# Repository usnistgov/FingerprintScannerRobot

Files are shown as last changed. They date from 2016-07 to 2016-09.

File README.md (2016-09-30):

# Fingerprint Scanner Robot v1.0

Welcome to the Fingerprint Scanner Robot project! This project is comprised of two robots to test fingerprint scanners. The first robot is the Networked Automated Fingerprint Scanner Test Robot (NAFSTR), and the second is the Networked Automated Rolled Fingerprint Scanner Test Robot (NARFSTR). Both robots were designed and built at the National Institue of Standards and Technology (NIST) as part of the [Biometric Web Services](http://www.nist.gov/itl/iad/ig/bws.cfm) project. The NAFSTR was designed and built by Jacob Glueck as part of the Summer High School Intern Program (SHIP) over the summer of 2014 and the NARFSTR was designed and built by Jacob Glueck during his time as a  Pathways Intern from October 2014 to July 2015 for the Biometric Web Services project. Kevin Mangold served as Jacob's mentor during both projects.

For more information, check out the documentation  at `Documentation/build/html/index.html` or `Documentation/build/latex/FingerprintScannerRobot.pdf`.

For a video of the NAFSTR, see: https://youtu.be/lXbDDAqTphQ.

For a video of the NARFSTR, see: https://youtu.be/WPvg-6ALE24.

## Project Contents:

For more detailed information and usage/installation details, see the Documentation/build artifacts.

* Circuit: contains all the files related to the robots' circuitry.
* Code: contains all the code
    * CSSharpLibrary: contains a Visual Studio C# solution with the CSharpLibrary for controlling the NAFSTR.
    * FingerprintRobotControl: contains an Eclipse Java project for controlling the robot.
    * FingerprintRobotLocalControl: contains all the C++ code that runs on the robots.
        * lib: libraries the code needs.
        * MACUploader: contains a program for uploading MAC addresses to the robots.
        * NAFSTRLocalControl: contains the program that controls the NAFSTR.
        * NARFSTRLocalControl: contains the program that controls the NARFSTR.
        * TestCode: contains test code.
* Documentation: contains all the documentation.
    * build: contains all the files for the built documentation.
    * source: contains all the source files for the documentation.
* DocumentationOld: contains the communication protocol for the NAFSTR, which is old.
* Final STL Files: contains all the STL files need to print parts for the robot.
* Fingerprints: contains all the files relating to fingerprints for the two robots.
    * NAFSTRSimpleFingerprints: contains all the files for the NAFSTR's fingerprints.
    * NARFSTRRolledFingerprints: contains all the files for the NARFSTR's rolled fingerprints.
    * PointCloudFingerprints: contains all the files for point cloud fingerprints.
* Improvements: contains files relating to improvements that need to be done.
* Pictures: contains pictures of the robots.
* Renderings: contains renderings of the robot.
* RobotLabels: contains files related to the information labels on the robots.
* Sketchup Files: contains the design files for the robots.
* Test STL Files: contains all the STL files used in test prints.
* Test Moves: contains text files with test commands for the two robots.
* Videos: contains videos of the robots.

## Contact:
Kevin Mangold (kevin.mangold@nist.gov)

## Credits:
Primary Developer: Jacob Glueck  
Support: Kevin Mangold

## Disclaimer:
See the NIST dislacimer at https://www.nist.gov/disclaimer.

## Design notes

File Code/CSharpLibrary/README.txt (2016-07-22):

1.	Move: the superclass of PositionMove and SensorMove. Represents a move as specified in the Arduino - Computer Communication Protocol.
2.	PositionMove: represents a position move as specified in the Arduino - Computer Communication Protocol.
3.	SensorMove: represents a sensor move as specified in the Arduino - Computer Communication Protocol.
4.	NAFSTR: represents a robot. Contains methods for each of the robot's commands.

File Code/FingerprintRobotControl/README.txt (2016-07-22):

This Java program allows for easy control of the robot.

1.	Instructions:
	To launch the GUI version, pass in no arguments. To launch the command line version, pass in two arguments. First, the name of the text file which contains the commands. Second, the location of the Arduino to connect to or the autoconnect preference. Acceptable values are a serial port name, an IP address, ethernet, or usb. "ethernet" sets the autoconnect preference to Ethernet and "usb" set the autoconnect preference to USB.
2. Classes:
	2.1	Arduino: represents a robot and is used to control the NAFSTR.
	2.2	ArduinoCom: represents a way of communicating with an Arduino.
	2.3	Command: represents an action that an Arduino can execute.
3. Javadoc: for more documentation, see the Javadoc at /doc/index.html

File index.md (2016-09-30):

---
layout: default
title: "Fingerprint Scanner Robot"
---
<script async type="text/javascript" id="_fed_an_ua_tag" src="https://dap.digitalgov.gov/Universal-Federated-Analytics-Min.js?agency=NIST&subagency=github&pua=UA-42404149-54&yt=true&exts=ppsx,pps,f90,sch,rtf,wrl,txz,m1v,xlsm,msi,xsd,f,tif,eps,mpg,xml,pl,xlt,c"></script>
# Fingerprint Scanner Robot v1.0

Welcome to the Fingerprint Scanner Robot project! This project is comprised of two robots to test fingerprint scanners. The first robot is the Networked Automated Fingerprint Scanner Test Robot (NAFSTR), and the second is the Networked Automated Rolled Fingerprint Scanner Test Robot (NARFSTR). Both robots were designed and built at the National Institue of Standards and Technology (NIST) as part of the [Biometric Web Services](http://www.nist.gov/itl/iad/ig/bws.cfm) project. The NAFSTR was designed and built by Jacob Glueck as part of the Summer High School Intern Program (SHIP) over the summer of 2014 and the NARFSTR was designed and built by Jacob Glueck during his time as a  Pathways Intern from October 2014 to July 2015 for the Biometric Web Services project. Kevin Mangold served as Jacob's mentor during both projects.

For more information, check out the documentation  at `Documentation/build/html/index.html` or `Documentation/build/latex/FingerprintScannerRobot.pdf`.

For a video of the NAFSTR, see: https://youtu.be/lXbDDAqTphQ.

For a video of the NARFSTR, see: https://youtu.be/WPvg-6ALE24.

## Project Contents:

For more detailed information and usage/installation details, see the Documentation/build artifacts.

* Circuit: contains all the files related to the robots' circuitry.
* Code: contains all the code
    * CSSharpLibrary: contains a Visual Studio C# solution with the CSharpLibrary for controlling the NAFSTR.
    * FingerprintRobotControl: contains an Eclipse Java project for controlling the robot.
    * FingerprintRobotLocalControl: contains all the C++ code that runs on the robots.
        * lib: libraries the code needs.
        * MACUploader: contains a program for uploading MAC addresses to the robots.
        * NAFSTRLocalControl: contains the program that controls the NAFSTR.
        * NARFSTRLocalControl: contains the program that controls the NARFSTR.
        * TestCode: contains test code.
* Documentation: contains all the documentation.
    * build: contains all the files for the built documentation.
    * source: contains all the source files for the documentation.
* DocumentationOld: contains the communication protocol for the NAFSTR, which is old.
* Final STL Files: contains all the STL files need to print parts for the robot.
* Fingerprints: contains all the files relating to fingerprints for the two robots.
    * NAFSTRSimpleFingerprints: contains all the files for the NAFSTR's fingerprints.
    * NARFSTRRolledFingerprints: contains all the files for the NARFSTR's rolled fingerprints.
    * PointCloudFingerprints: contains all the files for point cloud fingerprints.
* Improvements: contains files relating to improvements that need to be done.
* Pictures: contains pictures of the robots.
* Renderings: contains renderings of the robot.
* RobotLabels: contains files related to the information labels on the robots.
* Sketchup Files: contains the design files for the robots.
* Test STL Files: contains all the STL files used in test prints.
* Test Moves: contains text files with test commands for the two robots.
* Videos: contains videos of the robots.

## Contact:
Kevin Mangold (kevin.mangold@nist.gov)

## Credits:
Primary Developer: Jacob Glueck  
Support: Kevin Mangold

## Disclaimer:
See the NIST disclaimer at https://www.nist.gov/disclaimer.

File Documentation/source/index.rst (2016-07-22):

.. Fingerprint Scanner Robot documentation master file, created by
   sphinx-quickstart on Wed Jul 15 08:23:43 2015.
   You can adapt this file completely to your liking, but it should at least
   contain the root `toctree` directive.

Welcome to Fingerprint Scanner Robot's documentation!
=====================================================

.. toctree::
  :maxdepth: 2

  intro
  NARFSTR
  NAFSTR
  ProgramDevelopment
  Use

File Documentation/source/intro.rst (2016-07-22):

############
Introduction
############

The fingerprint scanner robots are designed to automatically test fingerprint scanners. There are two robots:

#. NAFSTR: Networked Automated Fingerprint Scanner Test Robot. A robot with four individually-actuated fingers that simulates simple fingerprinting.
#. NARFSTR: Networked Automated Rolled Fingerprint Scanner Test Robot. A robot that simulates rolling a finger across a fingerprint scanner.

Both robots are controlled by an Arduino Uno, and have an Arduino Ethernet Shield. They accept commands sent over USB and over a network.

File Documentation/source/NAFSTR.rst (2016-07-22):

.. include:: <isonum.txt>
.. include:: <isogrk1.txt>

######
NAFSTR
######

**Note:** The documentation below is sparse and needs to be improved. Have fun!

Design
======

Here is an image showing the main parts of the robot:



Here is an exploded view of the robot, which is helpful for assembly:



Here is an image showing how the finger attaches to the servo and how the fingerprint attaches to the finger:



Here is an image showing how the robot rests on the fingerprint scanner:



Here is a final image showing how the electronics housing is assembled:



Construction
============

To construct the robot, first print appropriate quantities of the parts in ``Final STL Files/NAFSTR``\ . Then, attach all the parts together and insert all the electronics. Here is a parts list of all the required parts that are not 3D printed:

.. csv-table:: Parts of NAFSTR
  :file: NAFSTRParts.csv
  :widths: 40,40,6,6,6
  :header-rows: 1

Electronics
===========

To assemble to electronics, look at the Fritzing file located at: ``Circuit/NAFSTRCircuit.fzz``\ .

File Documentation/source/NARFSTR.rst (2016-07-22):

.. include:: <isonum.txt>
.. include:: <isogrk1.txt>

#######
NARFSTR
#######

******
Design
******

Structure
=========

The robot has four adjustable legs, which support a linear actuator, the electronics, and the fingerprint assembly. The following image labels all the main parts:



Fingerprint Assembly
--------------------

The fingerprint consists of a fingerprint, held by two supports. A roller rolls over the fingerprint, pressing it against the scanner. The following image shows how it works:



The linear actuator pulls the roller towards the button. As the roller moves, it compresses the fingerprint against the scanner, causing the scanner the capture a rolled print. Once the moving assembly (consisting of the roller and its support structure) hits the button, the linear actuator stops, and then reverses.

Electronics Box
-------------------
The electronics box contains openings for all the connections and buttons on the robot. The following picture shows all the main features:



There are also four more openings on the back. These are to allow the linear actuator and the button in the fingerprint assembly to connect to the electronics in the box. The following image shows these connections:



************
Construction
************

Parts
=====

3D Printed Parts
----------------

Almost all of the parts for the robot are 3D printed. The STL files for the parts are located in ``Final STL Files/NARFSTR``\ . All of the 3D printed parts were printed in PLA except for the fingerprints. (For more information abou the fingerprints, see :ref:`fingerprintsection`\ .) The PLA parts were printed with a layer height of 0.2 mm using MakerBot's "Standard" profile. We used a MakerBot Replicator 2 and a  5\ :superscript:`th` Generation Replicator. The following table lists each part's name and quantity.

.. csv-table:: 3D Printed Parts
  :file: NARFSTR3DPrintedPartsList.csv
  :widths: 100, 25
  :header-rows: 1

Electronic Parts
-----------------

The following table lists all the electronic parts. Parts that are marked with \* are close to the parts I used, but may not be exact. This is because the parts I used came from kits or other sources, and I was unable to determine their exact information. For the male and female banana plugs, 3 different colors are recommended: 1 red, 1 black, 2 blue.

.. csv-table:: Electronic Parts
  :file: NARFSTROtherPartsList.csv
  :widths: 50, 16, 16, 16
  :header-rows: 1

Screws and Miscellaneous Parts
------------------------------

I did not order these parts, and so have limited information about them.

.. csv-table:: Screws and Miscellaneous Parts
  :file: NARFSTRScrewsAndFeet.csv
  :widths: 100 30 30
  :header-rows: 1

Here is a picture of the screws:



From now on, I will refer to the screws by their color.

Legs and Actuator Mount Assembly
================================

Legs
----

There are two leg assemblies: one on the side of the actuator with the motor, and one on the other side. Both are assembled the same way, but they use different leg adapters. To assemble a leg assembly, first screw a lock nut onto the threaded bolt in the center of the lower adjustable foot. Repeat for the other leg. Then, put an upper adjustable foot piece on top of each lower adjustable foot piece. Push down until the lock nut clicks, locking the lower part to the upper part. Then, insert a bolt head into the square hole on top of each upper adjustable foot. Screw the square head into the bolt using one of the black screws. Finally, connect each foot assembly to the lower part of a leg adapter. Secure the connection by screwing golden screws into the holes on the upper adjustable foot. Repeat this process with the other leg adapter to make the other leg assembly.



Actuator Mounts
---------------

There are two actuator mounts: one for the side of the actuator with the motor, and one for the other side.

Motor End Actuator Mount
""""""""""""""""""""""""

Slide the actuator into the mount. Insert the motor end actuator key into the hole in the actuator mount. Make sure the arrows point towards each other. Secure the key with a golden screw.



Finger End Actuator Mount
"""""""""""""""""""""""""

Slide the actuator into the mount. Insert the finger end actuator key into the hole in the actuator mount. Make sure the arrows point towards each other. Attach the top actuator strap to the actuator using two golden screws.



Insert the bottom actuator strap as shown in the diagram below. Secure it with two black screws. Finally, screw a golden screw into the hole labeled "Screw Hole for Actuator Key" on the diagram below. This secures the key.



Put a 12 mm push button into the button hole on the actuator mount. Secure the button using the button strap and two black screws.



Insert the finger end fingerprint mount and the motor end fingerprint mount into the bottom of the actuator mount. Secure each one with two black screws. Then, insert a fingerprint clip into each of the fingerprint mounts.



Connecting the Legs and Actuator Mounts
---------------------------------------

Insert the leg assemblies into the bottom of the actuator assembly. Secure each leg assembly with two golden screws.



Rubber Feet
-----------

Insert two rubber feet into the bottom of each foot.

Fingerprint Assembly
====================

Glue fingerprint roller A into fingerprint roller B using super glue. Let dry. Connect fingerprint roller to moving base with the exterior finger supports. Secure each support with two black screws. Insert the button pusher into the moving base.



Attach the fingerprint assembly to the actuator by first aligning the four holes on the moving base with the holes on the actuator, ensuring that the button pusher faces the button. Then, screw a silver screw into each of the four holes on the moving base.



Electronics Box Assembly
========================

**Note:** assemble the electronics before assembling the box.

Slide Arduino Uno (with Arduino Ethernet Shield) into the box. Screw female banana plugs into holes of electronics housing. If using colors, put a red jack and a black jack into the top row, and put two blue jacks in the bottom row. Then, super glue the LED cap into the LED hole.



Super glue the front tab onto the bottom of the electronics box.



Assemble the top lid by inserting the power switch and the trigger switch into their holes. The power switch is the green rocker switch, and the trigger switch is the red push button. Using epoxy, glue a 12 mm button into the DHCP reset button hole. The square base of the button should be glued onto the plastic square on the bottom of the top lid.



Assemble the power jack by inserting a female power pigtail into the power jack holder. This may require some force. Screw power jack holder into electronics box using a black screw.



Put all other electronics into the box in the empty area behind the Arduino and put LED into LED cap. Ensure that everything is properly connected. Then, put top on box and secure with two black screws. Put back side on box and secure with one black screw. Finally, connect all cables.

***********
Electronics
***********

Design
======

The robot is controlled by an Arduino Uno microcontroller. On top of the Arduino, there is an Arduino Ethernet Shield, which, through its single Ethernet port, allows the robot to connect to a network. The following components are connected to the Arduino through the header pins on the shield:

#. RGB LED: serves as an indicator light.
#. Trigger switch: a red pushbutton, causes the robot to move its finger back and forth when pressed.
#. Limit switch: a 12 mm push button which detects when the fingerprint has finished rolling.
#. DHCP reset button: a 12 mm push button, causes the robot to request a DHCP lease.
#. Pololu VNH5019 motor driver chip: used to drive the linear actuator.

The robot has a single 2.1 mm DC barrel jack for power and requires 12 V DC at around 3A (estimated; based on peak motor current draw). The 12 V lines are attached directly to the motor control board, and the Arduino is powered by the output of a 5V Universal Battery Elimination Circuit (UBEC). The UBEC can produces a regulated 5 V output at a current of up to 3A. This works far better than the Arduino's built-in regulator, which, though it can handle 12 volts, gets very hot when doing so and has trouble providing the necessary current for both the Arduino and the Ethernet Shield. The robot also has a power switch, which is connected to the 12 V input line.

Here is a schematic:



There is no Ethernet Shield in the schematic, but it would be placed on top of the Arduino.

Assembly
========

First, put the Arduino Ethernet Shield onto the Arduino. Then, on the 5 cm x 7 cm perfboard, assemble the circuit using the schematic above. For the motor and limit switch, which are mounted outside of the box, connect their leads to the female banana plugs, which will go into holes on the side of the electronics box. On the ends of the leads for the motor and button (which will be outside the box), attach the male banana plugs. Use the two blue plugs for the button's leads, the red one for the motor's red wire, and the black one for the motor's black wire. For the LED and other buttons, make sure they are connected with long wires so they can reach from the circuit board to their designated location in the box. Also, do not directly connect any components that will be mounted in the box directly to the circuit board. You will not be able to put the components into their holes. Instead, use the tab connectors to attach the component to the rest of the circuit. Finally, on all the 12 V lines (which, because they are connected to the motor, would have high currents), use the 20 gauge wire.

.. _fingerprintsection:

************
Fingerprints
************

The fingerprints used on the robot are 3D printed. The first step in making a fingerprint is to generate a PNG image of the fingerprint. To do this, I used `SFinGe <http://biolab.csr.unibo.it/research.asp?organize=Activities&select=&selObj=12&pathSubj=111%7C%7C12&>`_ (**S**\ ynthetic **Fin**\ gerprint **Ge**\ nerator) from the Biometric System Laboratory at the University of Bologna . With the program, I configured various parameters of the fingerprint, and once the ridges were generated, clicked the "View original" button after every step to remove all the distortion and scratches. Once the fingerprint was generated, I saved it to a bmp file and then converted it to a png.

To turn the PNG into a 3D-printable file, I wrote an OpenSCAD script, located at ``Fingerprints/NARFSTRRolledFingerprints/roll.scad``\ . This script can take any black and white PNG image and produce a STL file that, when 3D printed, will fit perfectly into the robot. To use the script, configure the variables at the top of the file::

  imageResolution = 19.7; //dots per mm
  imageX = 416; //px
  imageY = 560; //px
  file = "FGen1.png";
  fingerprintX = 30; //mm
  fingerprintY = 30; //mm
  fingerprintScale = 1.4;

Once these variables are configured, hit "Preview" in OpenSCAD to make sure everything looks good, and then hit "Render". This may take about an hour. Once the rendering is complete, export the file as an STL.

This script will generate a very complex 3D file which contains the fingerprint, mounted on a spongy area, which is mounted on tabs that connect to the robot. Here is a cross-sectional view of the finished product:



The two tabs at either end allow the fingerprint to be secured to the robot. The fingerprint is on top of the raised area in the middle. The holes in the raised area allow the fingerprint to compress, which results in a better scan. Here is a close up view of the holes:



To 3D print the STL file, use MakerBot Flexible Filament. Be sure to set the printing profile to the custom profile located at ``Fingerprints/ NARFSTR Rolled Fingerprints/fingerprintprofile.txt``\ . The custom profile, which is based off of the MakerBot flexible filament profile, uses 1 shell and an extruder temperature of 140 |deg|\ C.

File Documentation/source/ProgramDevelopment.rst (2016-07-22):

###################
Program Development
###################

There are two programs associated with each robot: (1) a Java program that runs on a computer and controls the robot and (2) a C++ program that runs on the robot. The Java program works with both a Graphical User Interface (GUI) and the command line. With the GUI, the user specifies the actions for the robot to execute, and then connects to the robot and executes the actions. With the command line, the user can supply a text file of commands for the robot to execute, and the program will send the commands to the robot. The C++ program on the robot receives all the commands and executes them. It also responds to any button presses.

Java Robot Control Program
==========================

The Java program has 3 main parts:

#. The back end, which handles all communication with the robot.
#. The GUI, which provides a simple way to control the robot.
#. The command line interface, which lets the user send a list of commands to the robot.

This guide will explain each of the three parts.

Back End
--------

The back end consists of the robot package, which contains four main classes:

#. ``Robot``
#. ``RobotCom``
#. ``RobotInfo``
#. ``Command``

``Robot`` is an abstract class, and it represents any type of robot, either a NAFSTR or a NARFSTR. It currently has one subclass, ``NARFSTR``. The current version of the program does not support the NAFSTR robot; to control a NAFSTR, the older version must be used. ``NARFSTR`` has one constructor, which takes a ``RobotCom`` object. A ``RobotCom`` is a channel for communicating with the robot, and has methods for reading and writing data. ``RobotCom`` has two subclasses: ``SerialRobotCom``\ , which represents a connection to a robot over a serial port (USB), and ``NetworkRobotCom``\ , which represents a connection to a robot over a network. In order to make an instance of either class, a ``RobotInfo`` object is required. A ``RobotInfo`` object describes the type of robot, the location of the robot (an IP address and a serial port), and the robot's MAC address, which is used as an ID.

In order to easily find robots, the ``Robot`` class provides three static methods:

#. ``findSerialRobots()``\ : finds all the robots connected over USB by checking every USB port.
#. ``findNetworkedRobots()``\ : finds all the robots connected over the network by sending out a UDP broadcast and listening for responses.
#. ``findRobots()``\ : finds all the robots over both USB and the network.

In order to execute commands on a robot, the ``Robot`` class provides an ``executeCommand(Command c)`` method, and an ``executeCommands(List<Command> commands)`` method. Both methods send commands to the robot, and wait for execution to finish. A ``Command`` object consists of two components: a String representing the command name, and a list of Objects representing the parameters.

For more documentation, see the Javadoc, in ``Code/FingerprintRobotControl/doc``\ .

GUI
---

The code for the GUI is in three packages: ``view``\ , ``view.configurator``\ , and ``view.robotpanel``\ . The program's GUI is an instance of ``view.RobotController``\ . The ``RobotController`` class has two main components: a ``view.robotpanel.RobotConnectionPanel``\ , which manages the connection with the robot, and a ``view.robotpanel.CommandEditorPanel``\ , which allows the user to edit the commands being sent to the robot.

Command Line
------------

The code for the command line interface is in ``main.FingerprintRobotControl``\ . When ``FingerprintRobotControl`` is executed with no arguments, it automatically creates an instance of ``view.RobotController``\ , creating the GUI. If there are arguments, it attempts to use them. The argument format is: ``<robot type> <file name> <connection location>``\ . The robot type should be either NAFSTR of NARFSTR. (NAFSTR is not currently supported, but will be soon.) The file name should be an absolute or relative path to the file of commands which the program is to execute. The file format is a text file with one command per line. Finally, the connection location could be one of four things: "ethernet", "usb", an IP address, or a serial port. If it is "ethernet" or "usb", to program will search for robots connected over the specified channel, and pick the first one.

C++ Local Control Program
=========================

Development Environment
-----------------------

The program was developed in Eclipse using the the Arduino Eclipse Extensions version 2.4.201506210212 by Jan Baeyens (http://www.baeyens.it/eclipse/), with the Arduino libraries version 1.6.5. The Robot's program consists of two parts: C++ libraries which are common to both robots (the libraries are currently only used with the NARFSTR, but should be used on the NAFSTR), and a ``.ino`` file which contains the main program for the robot. The ``FingerprintRobotCom`` library is stored in ``Code/FingerprintRobotLocalControl/lib``\ . In order to make the Arduino plugin include this library (and other libraries which are stored in the lib folder) in the build path, the "Private Library Path" in the Arduino Plugin Preferences must be set to ``Code/FingerprintRobotLocalControl/lib``\ .

Libraries
---------

The code needs several libraries in order to compile. First, it needs the ``FingperintRobotCom`` library, which handles communication between the robot and the computer. Second, it needs the ``EthernetNonBlocking`` library, which is a modified version of the standard Arduino Ethernet Library. I modified the standard library to make the DHCP functions non-blocking. This significantly improves responsiveness; with the standard blocking DHCP functions, the robot would freeze for 60 seconds if no Ethernet cable was plugged in. Both programs also need the following standard Arduino libraries:

#. ``EEPROM``
#. ``SPI``

Each of the NAFSTR and NARFSTR programs also require some specific libraries:

NAFSTR

  #. ``Servo``\ : standard Arduino library.

NARFSTR

  #. ``Arduino-RGB-Tools``\ : an open-source library for controlling RGB LEDs. It is on github (https://github.com/joushx/Arduino-RGB-Tools), stored in the git repository as a submodule, and licensed under The MIT License (MIT).
  #. ``RGBConverter``\ :  an open-source library for converting between RGB and HSV. It is on github (https://github.com/ratkins/RGBConverter), stored in the git repository as a submodule, and its license says that you can do whatever you want with it.
  #. ``VNH5019Driver``\ : a library I wrote for controlling the VNH5019 driver chip.

NARFSTR
-------

The NARFSTR control program is located at ``Code/FingerprintRobotLocalControl/NARFSTRLocalControl``\ . Its main file is ``NARFSTRLocalControl.ino``\ .

NAFSTR
------

The NAFSTR control program is located at ``Code/FingerprintRobotLocalControl/NAFSTRLocalControl``\ . Its main file is ``NAFSTRLocalControl.ino``\ . The NAFSTR program is old, and so does not use either the ``FingerprintRobotCom`` library or the ``EthernetNonBlocking`` library.

Development Information
-----------------------

The ``FingerpintRobotCom`` library attempts to read a MAC address from the Arduino's EEPROM on startup. If no MAC address is found, it will not work. In order to load a MAC address into EEPROM for the first time, use the ``MACUploader`` program located at ``Code/FingerprintRobotLocalControl/MACUploader``\ .

``FingerprintRobotCom`` Library
^^^^^^^^^^^^^^^^^^^^^^^^^^^^^^^

The ``FingerprintRobotCom`` library header file (located at ``Code/FingerprintRobotLocalControl/lib/FingerprintRobotCom/FingerprintRobotCom.h``) contains comments which explain all the important functions.

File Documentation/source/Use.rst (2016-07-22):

################
Using the Robots
################

The robots are controlled by text commands send to them over either a serial connection, a TCP network connection, or a UDP network connection. These text commands can be sent in many ways. They can be sent through the Java control software, using both the command line interface and the GUI, they can be sent using Telnet or Putty, and they can be sent using serial terminal, such as gtkterm. This guide will explain the command format, and how to send commands using all the different channels.

Communication Protocol
======================

Protocol
--------

General Information
"""""""""""""""""""

#. The robot will receive input from a serial stream via USB or over a network connection on port 2424 (the NAFSTR uses port 80 because its software is old) via Ethernet. The format of the requests will be the same in all cases.
#. When the robot is connected over the network, it is capable of receiving requests over both a UDP connection and a TCP connection. However, if any request is received over a UDP connection, the response message will be sent over a TCP connection.
#. With the exception of UDP messages as mentioned above, the robot will respond to all messages over the channel the message was received on.
#. The robot only has a 64 byte serial buffer. Thus, if many commands are sent rapidly over USB, some commands will be lost. However, when connected over Ethernet, the robot has a 16 kibibyte buffer, thus making an overflow less likely.

Format
""""""

#. Each command has the format ``commandName arg_0 arg_1 arg_2...``\ , where ``arg_n`` is the n\ :superscript:`th` argument. If the command has no arguments, then the command is simply the name. Each part of the command is separated from the others with a single space.
#. Upon receiving and successfully parsing a command, the robot will send a message of the format ``commandName-received``\ . If there is a problem parsing a command, the robot will instead send ``bad-command``\ .
#. Upon completion of a command, the robot will send a message of the format ``commandName-end``\ .\
#. When sent the string “fingerrobot”, the robot will respond with a string of the format: ``found:robot type:MAC Address:``\ . For example, a NARFSTR robot with a MAC address of ``ba:db:ad:ba:db:ad`` would respond with ``found:NARFSTR:ba:db:ad:ba:db:ad:``\ .

Commands
--------

NARFSTR Commands
""""""""""""""""

:Stroke:
  :Description: causes the robot to move the finger through one cycle.
  :Format: ``stroke``
:Set:
  :Description: sets the parameters of the robot's following moves.
  :Format: ``set forwardSpeed buttonWaitTime reverseSpeed returnWaitTime``
  :Parameters:
    :``forwardSpeed``: the motor's speed when driving the finger away from the starting position. Between 0 and 255, inclusive.
    :``buttonWaitTime``: the amount of time, in ms, the robot should wait once the finger hits the limit switch.
    :``reverseSpeed``: the motor's speed when driving the finger back to the starting position. Between 0 and 255, inclusive.
    :``returnWaitTime``: the amount of time to wait, in ms, once the finger has returned to its original position.
:Reset:
  :Description: causes the robot the drive the finger towards the starting position.
  :Format: ``reset time speed``
  :Parameters:
    :``time``: the amount of time the finger will be in motion, in ms.
    :``speed``: the motor's speed, between 0 and 255 inclusive.

NAFSTR Commands
"""""""""""""""

See ``DocumentationOld/Arduino - Computer Communication Protocol.docx`` or ``DocumentationOld/Arduino - Computer Communication Protocol.txt`` for details.

Examples
--------

The following are examples of what an exchange with the robot would look like.

NARFSTR Example
"""""""""""""""

::

  fingerrobot
  found:NARFSTR:90:a2:da:0f:95:39:
  set 120 2000 120 2000
  set-received
  set-end
  stroke
  stroke-received
  stroke-end
  reset 1000 255
  reset-received
  reset-end
  notacommand
  bad-command

NAFSTR Example
"""""""""""""""
Please put one here!

Control with ``FingerpintRobotControl`` Java Program
====================================================

The program can be found in ``Code/FingerprintRobotControl/FingerprintRobotControl-v1.1.jar`` and allows for both GUI and command line operation. The following two sections describe both methods.

**Note:** the NAFSTR uses an older version of the software, found in ``Code/FingerprintRobotControl/FingerprintRobotControl-v1.0.jar``\ . Most, but not all, of the instructions below apply to the older version.

GUI Control
-----------

To launch the program in GUI mode, simply run the program. Or, launch the program from the command line with no arguments: ``java -jar FingerprintRobotControl-v1.1.jar``\ . Once the program opens, you should see a window like the one below.



This is the starting screen. To use the program, first search for robots by clicking the "Search" button. After about three seconds, the combo box will be populated with the types, locations, and MAC addresses of all the robots the program found. To connect to a robot, select one from the list and press connect. If the connection was successful, the status field to the left of the combo box should say "Connected".

Now, you can begin to write the commands you want the robot to execute. There are two ways to do this: (1) using the graphical configurator, which requires no knowledge of the communication protocol or, (2), using the text configurator, which allows you to simply type the commands you wish to send to the robot. To use the graphical configurator, press the button on the bottom of the screen with the name of the command you wish to add. A command should show up on the screen. Now, type in the specified values. A complete graphical program looks like the one below.



To use the text configurator, select the tab labeled "Text Configurator". If you have a program currently open if the graphical configurator, it will automatically be converted to text and displayed in the text configurator. This is a good way to learn the text format of the commands. Once you are in the text configurator, simply type commands. A program written with the text configurator is shown below:



Once you are done with you program, you can save it by going to "File" menu and clicking "Save". This will bring up a dialog asking you where you would like to save your file. The saved files are plain text files, with the same content that appears in the text configurator. To open a file, choose "Open" from the "File" menu. When you open a file, there will be radio buttons on the right side of the open dialog to allow you to choose the type of robot the opened file is for. (Currently, there is only one button for the NARFSTR. Support will be added for the NAFSTR in the future.) The picture below shows the open dialog.



To execute your programs, hit the "Execute" button. This will send the commands to the robot. You can see the progress in the progress bar. If you want to stop execution, hit the "Stop" button. This will stop execution after the currently running move is complete. There is no way to stop execution in the middle of a move. If you click the stop button, and the program still says "Stopping" under the progress bar even though the robot has stopped, you may need to click the "Force Stop" button. This will immediately disconnect the robot.

Command Line Control
--------------------

To run the program from the command line, use the following command:

``java -jar FingerprintRobotControl-v1.1.jar robotType fileName connectionMode``

:Parameters:
  :``robotType``: the type of robot to control, either NAFSTR or NARFSTR. (Currently only NARFSTR is supported.)
  :``fileName``: an absolute or relative path to a file containing the commands to execute, 1 command per line.
  :``connectionMode``:
    :``ethernet``: searches for robots on the network and connects to the first one found.
    :``usb``: searches for robots connected over USB and connects to the first one found.
    :IP address: the IP address of the robot to connect to.
    :Serial port: the name of a serial port the robot is plugged into.

Control Using Telnet, Putty, and other Terminals
================================================

The robot can easily be controlled using any terminal. With telnet, simply type ``telnet ipAddress 2424``\ , where ``ipAddress`` is the IP address of your robot. With Putty, enter the IP address of your robot and the port 2424. Then, select telnet for the protocol and hit connect. For gtkterm, launch the terminal and select the right serial port. Once you have connected your terminal, just type commands, 1 per line, and the robot should execute them.

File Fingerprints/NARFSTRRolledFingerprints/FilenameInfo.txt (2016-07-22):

The fingerprint files generated from PNG files with roll.scad are named using the following format:
[PNG file name]S[scale factor]X[fingerprint X dimension (mm)]Y[fingerprint y dimension (mm)]R[ridge height (mm)]

A suffix of BF means it has tabs that extend out on the side. A suffix of LF means it has tabs that are the proper size to allow it to fit into the NARFSTR. No suffix means it has tabs, but they are right next to the fingerprint.

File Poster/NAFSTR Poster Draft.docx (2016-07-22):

# NAFSTR: Networked Automated Fingerprint Scanner Robot

1. Features:
  1.1. Four independently actuated fingers
  1.2. Interchangeable fingerprints
  1.3. Can detect when the scanner has captured a fingerprint
  1.4. Can monitor force being applied to each finger
  1.5. Controllable through a serial connection over USB, through a TCP connection over Ethernet, and through a UDP connection over Ethernet.
2. How it works:
  2.1. Fake Fingerprints:
    2.1.1. 3D printed in MakerBot Flexible Filament.
    2.1.2. Consist of 3 layers: .2 mm thick plastic backing, .2 mm thick fingerprint and 8 mm thick foam.
    2.1.3. <Insert Image>
  2.2. Finger Motion and Sensors:
    2.2.1. Each finger is connected to a servo motor which can provide about .8 N⨯m of torque.
    2.2.2. Each fake fingerprint is mounted onto a fingerprint holder. Sandwiched between the holder and the fake fingerprint is a Force Sensitive Resistor (FSR).
    2.2.3. The fingerprint scanner has 4 lights which turn green when the fingerprint has been read. The robot uses 4 Light Dependent Resistors (LDR), one for each light on the fingerprint scanner, to determine when the lights turn green.
    2.2.4. <Insert Picture>
  2.3. Control
    2.3.1. The robot accepts text commands over USB and Ethernet. When operating over Ethernet, the commands can be send over either TCP or UDP.
    2.3.2. The robot stores one move for each finger. The move can be changed by sending a set command.
    2.3.3. When the robot receives a move command, it reads the stored moves for the selected fingers and moves the fingers.
    2.3.4. Move Types:
      2.3.4.1. Position moves: the robot moves one of the fingers to a specified position and waits for a specified amount of time.
      2.3.4.2. Sensor moves: the robot moves one of the fingers at a specified angular velocity until the reading from the light sensor moves into a certain range or the fingers position has exceeded a specified limit. When the sensor move ends, it reads the force sensor to determine how much force was exerted on the fingerprint scanner.
    2.3.5. Communicating with the robot
      2.3.5.1. There is an easy to use graphical Java program that allows the user to connect to the robot and send it commands.
      2.3.5.2. <Insert picture>
      2.3.5.3. The same Java program, when run from the command line, can send a text file of commands to the robot for execution.
      2.3.5.4. Commands can also be sent over Telnet.
      2.3.5.5. C# and Java libraries to control the robot.
3. Uses
  3.1. Stress testing for WS-BD standard.
    3.1.1. The robot could put thousands of finger combinations down onto the scanner to see if the scanner adheres to the WS-BD standard. The robot could operative for days for a long term test.
  3.2. Analyzing spoof detection methods
    3.2.1. The robot can place fingerprint spoofs with a consistent position and consistent, selectable force onto fingerprint scanners. This process could be repeated for hours and with different forces and fingers prints to determine how well spoof detection methods work.

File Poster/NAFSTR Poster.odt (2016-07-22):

# NAFSTR: Networked Automated Fingerprint Scanner Test Robot

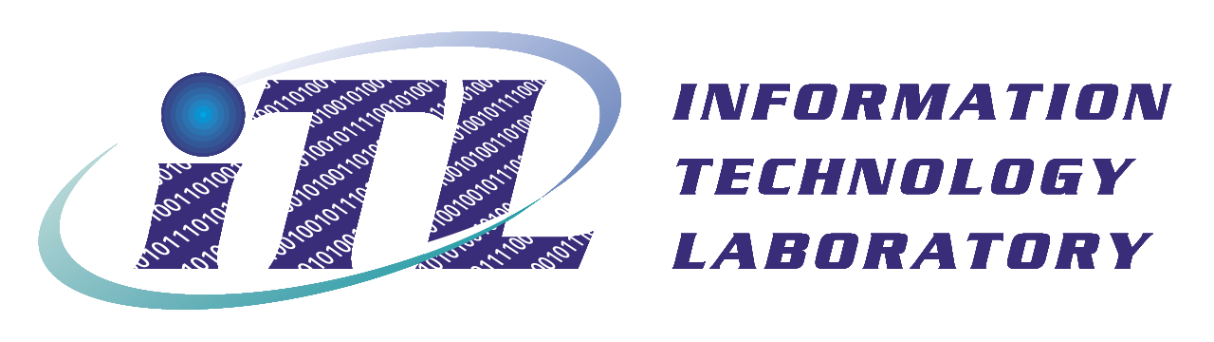
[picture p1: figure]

| Jacob Glueck

### NAFSTR uses fingerprint spoofs and four independent fingers to test fingerprint scanners.

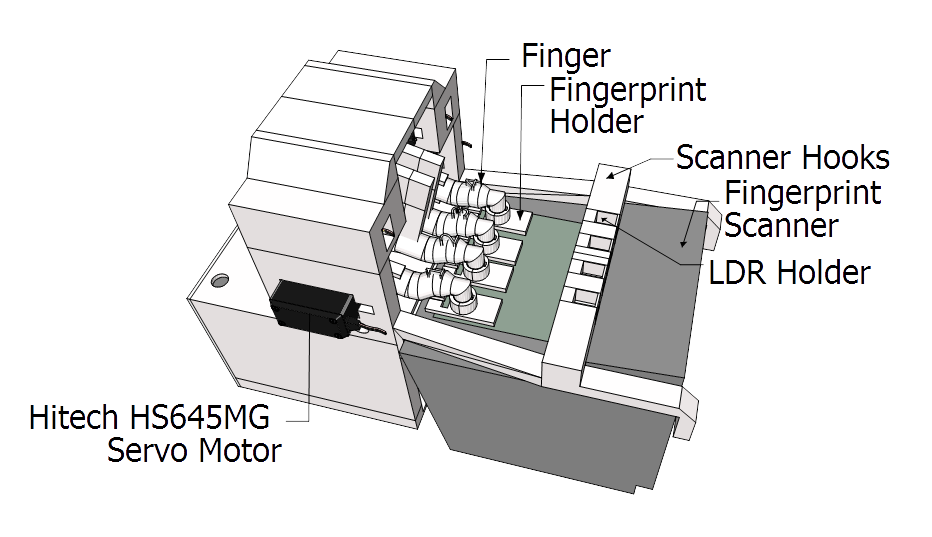
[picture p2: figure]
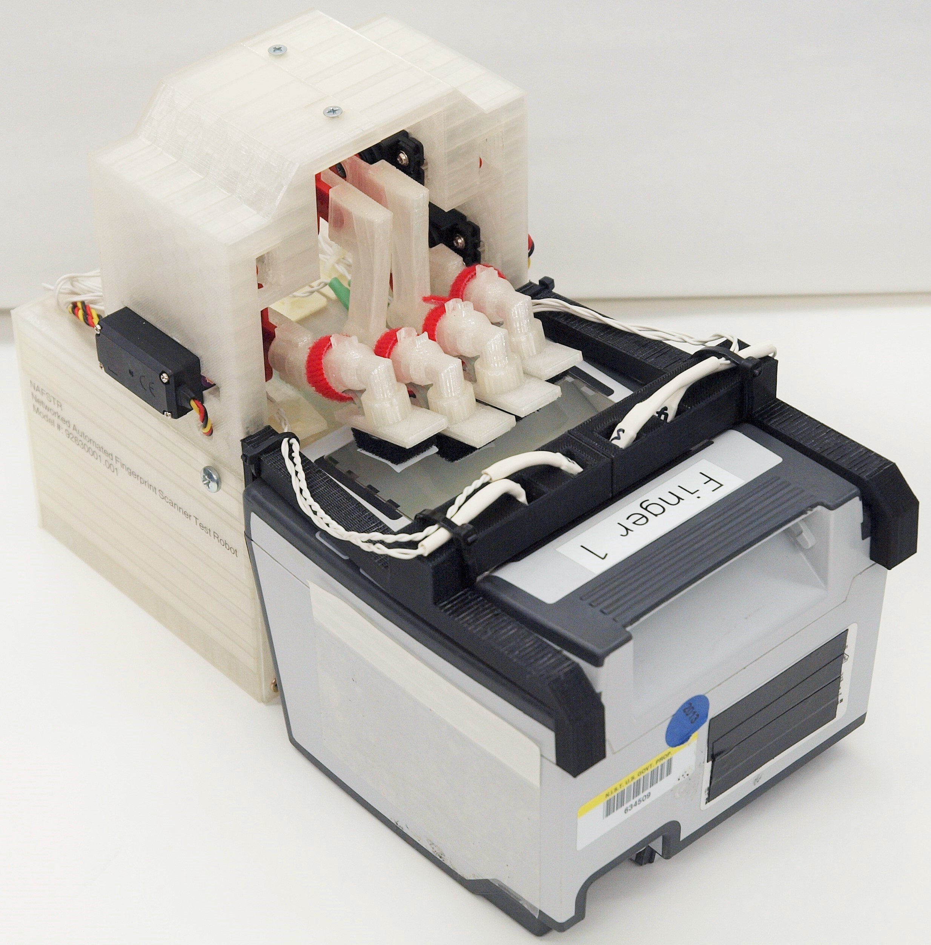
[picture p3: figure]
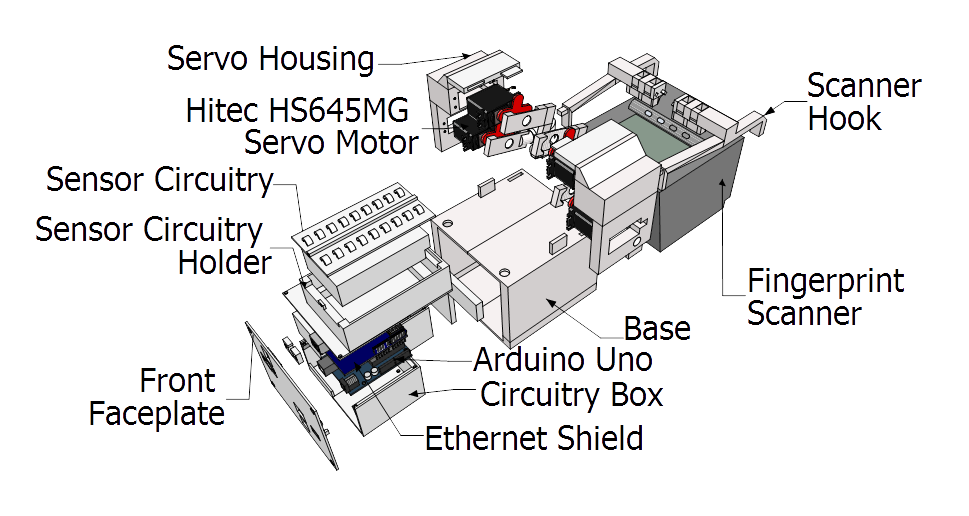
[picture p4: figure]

Illustration 1: Labeled front view of NAFSTR. | Illustration 2: Photograph of NAFSTR with fingerprint scanner. | Illustration 3: Labeled exploded view of NAFSTR's parts.

#### Features

- Four independently actuated fingers.
- Interchangeable fingerprints.
- Can detect when the scanner has captured a fingerprint.
- Can monitor force being applied to each finger.
- Controllable through a serial connection over USB, through a TCP connection over Ethernet, and through a UDP connection over Ethernet.
- Controllable over Telnet.
- Can move each finger to a specified position or until the scanner captures a fingerprint.

#### Construction

- All parts were 3D printed.

#### Fingerprint Spoofs

- 3D Printed:
  - Simple arrangement of thick lines and curves 3D printed in MakerBot Flexible Filament.

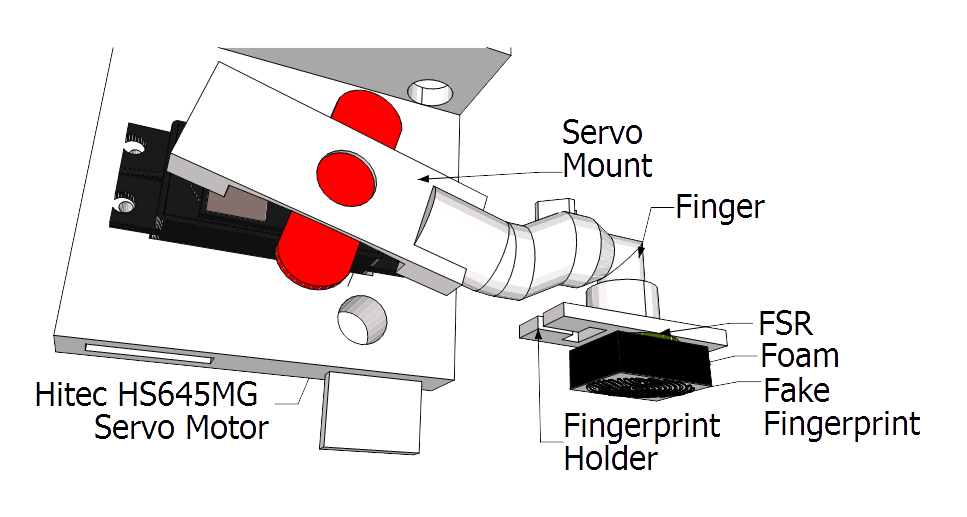
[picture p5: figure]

  - 0.4 mm thick 3D printed fingerprint mounted to 8 mm thick foam. Illustration 4: Labeled view of finger and fingerprint.
- Gelatin
  - Made by pouring gelatin and graphite into a fingerprint mold.

#### Uses

- Stress testing for Web Services-Biometric Devices (WS-BD).
  - WS-BD is a standard for communication with biometric devices using web services.
  - The robot could operate for days and put thousands of finger combinations down onto the scanner.
- Analyzing spoof detection methods
  - The robot can place fingerprint spoofs with a consistent position and consistent, selectable force onto fingerprint scanners. This process could be repeated for hours with different forces and fingerprints to determine how well spoof detection methods work.

#### Finger Motion and Sensors

- Each finger is connected to a servo motor which can provide about 0.8 N·m of torque.
- Each fake fingerprint is mounted onto a fingerprint holder.
- Sandwiched between the holder and the fake fingerprint is a Force Sensitive Resistor (FSR).

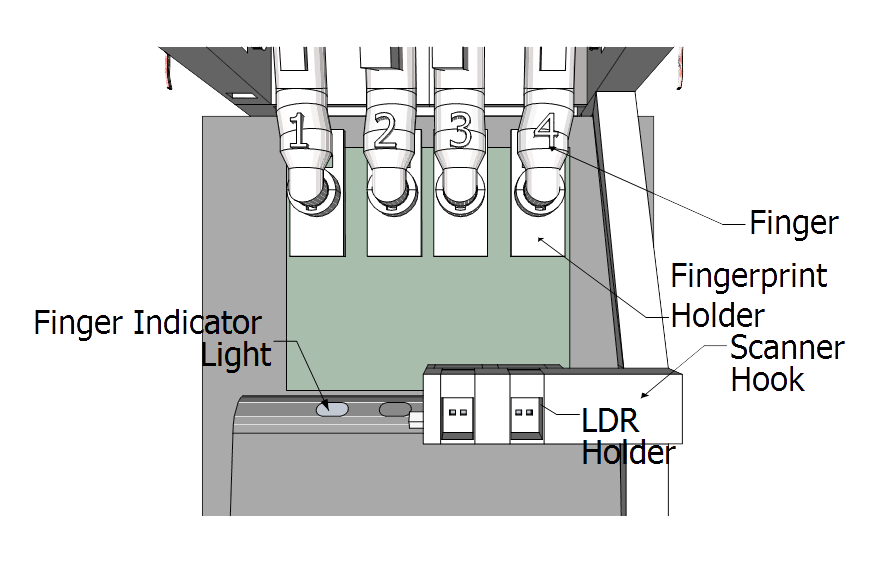
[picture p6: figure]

- The fingerprint scanner has 4 lights which turn green when the fingerprint has been read. The robot uses 4 Light Dependent Resistors (LDRs), one for each light on the fingerprint scanner, to determine when the lights turn green. Illustration 5: Labeled top view of scanner and NAFSTR.

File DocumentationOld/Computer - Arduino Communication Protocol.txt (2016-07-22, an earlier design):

Computer - Arduino Communication Protocol
This document describes the communication between the fingerprint robot and the computer.
1.	Communication
1.1.	The Arduino will receive input from a serial stream via USB or over a network connection on port 80 via Ethernet. The format of the requests will be the same in both cases.
1.2.	When the Arduino is connected over the network, it is capable of receiving requests over both a UDP connection and a TCP connection. However, if any request is received over a UDP connection, the response message will be send over a TCP connection.
2.	Verification
2.1.	There may be many devices on the network and connected via USB. As such, the Arduino must be identifiable. When a computer connects to a device, the computer should transmit the string "fingerrobot" to the device. If the device is indeed the fingerprint robot, it should respond with the string "youfoundme" and thus confirm its identity. This should allow a computer to easily determine which device is the Arduino.
3.	Communication
3.1.	Moves
3.1.1.	A move describes the motion of one servo motor. There are two types of moves: position moves and sensor moves.
3.1.1.1.	Position Moves
3.1.1.1.1.	A position move is when a servo motor moves to a specified position. Each position move consists of two parameters: the target servo position and the time allotment. For a position move, a command is sent to the servo to move to the specified position. During the time allotment, which starts as soon as the Arduino sends the command to the servo, no other commands will be sent to the servo.
3.1.1.1.2.	Format: pos <absolute position (degrees)> <time allotment (ms)>
3.1.1.2.	Sensor Moves
3.1.1.2.1.	A sensor move is when a servo motor moves until its sensor readings indicate that it is finished. Each sensor moves consists of 5 parameters: the servo’s angular velocity, the minimum light threshold, the maximum light threshold, the position threshold, and the wait time. For a sensor move, the servo will rotate at the specified speed until sensors indicate that the move is complete. Then, the servo will wait for the specified time. The sensors will indicate that the move is complete when the servo’s target position goes past the position threshold (if the servo is rotating forwards, it will stop when its position is greater than the position threshold, if the servo is rotating backwards, it will stop when its position is less than the position threshold) or the light sensor reading is between the maximum and minimum values.
3.1.1.2.2.	Once the waiting period has completed, the Arduino will return one of two possible values. If the sensor move completed because the light sensor reading moved into an acceptable rage, the Arduino will return a string of the following format: finger-<finger number>-successful-<force>.  If the move finishes because the servo the position threshold is exceeded, the Arduino will return a string of the following format: finger-<finger number>-failed-<force>.
3.1.1.2.2.1.	The force returned will be the value from the force sensor when the move finishes.
3.1.1.2.3.	Format: sen <speed (degrees/second, a negative value means the servo will rotate backwards)> <lower light threshold, inclusive, in the range [0, 1023]> <upper light threshold, inclusive, in the range [0, 1023]> <position threshold (degrees)> <wait time (ms)>
3.2.	Finger Moves
3.2.1.	A finger move is two servo moves; one move that places the finger down onto the fingerprint scanner and one move that lifts the finger off the scanner.
3.2.2.	The finger move data is stored in a string. The finger move is simply the concatenation of two servo moves.
3.3.	Command
3.3.1.	The following describes the command set that the Arduino will use.
3.3.2.	Set command
3.3.2.1.	The set command causes the Arduino to set move data for 1 servo.
3.3.2.2.	Format: set <servo number> <finger move>
3.3.2.3.	The servo number will be in the range [0, 3]. The move will be in the notation described in section 2.2.2. This method returns the string “set-end” upon completion of the move.
3.3.3.	Move command
3.3.3.1.	The move command causes the Arduino to execute the stored move data, for specified servos.
3.3.3.2.	Format: move <number of servos> <servo ...>
3.3.3.3.	The command takes a list of space-separated servo numbers and executes their moves synchronously. The number of servos should be the first argument. If the first argument is 0, every servo’s move is executed. For example, move 2 1 2 would move servos 1 and 2. move 0 would move all the servos. This method returns the string “move-end” upon completion of the move.
3.3.4.	Get command
3.3.4.1.	The get command returns a sensor value. The command can get the value of any of the 4 FSRs and any of the 4 LDRs.
3.3.4.2.	Format: get <servo> <sensor>
3.3.4.3.	The command takes two parameters. First, the servo number that is associated with the desired sensor. Second, the desired sensor type, either “f” or “l”. For example, get 3 f would get the FSR value for the FSR on servo 3. The value will be returned as a string, over the stream that the computer is using to communicate with the robot.
3.3.5.	Relax command
3.3.5.1.	Relaxes the servos so that the fingerprints can be changed.
3.3.5.2.	Format: relax
3.3.6.	Hold command
3.3.6.1.	Puts the servos back to their original positions.
3.3.6.2.	Format: hold
3.4.	Once the Arduino has received and started the execution of a command, it will return a string in the following format: “<command name>-received” and then proceed to execute the command. Once the received message has been sent, the Arduino will be able to receive another command. However, if two commands are sent in close succession, and the second command arrives before the Arduino has sent the received message for the first command, the second command may be lost due a buffer overflow on the Arduino. When connected over USB, the Arduino has a very small 64 byte buffer, making an overflow likely. However, when connected over Ethernet, the Arduino has a 16K byte buffer, thus making an overflow less likely.
3.5.	Once the Arduino has finished a command, it will return a string in the following format: “<command name>-end”.
3.6.	If the Arduino receives a bad command, it will return the following string: “bad-command”.

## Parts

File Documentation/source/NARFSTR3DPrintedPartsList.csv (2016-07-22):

Part Name | Quantity
Actuator Mount - Finger End | 1
Actuator Mount - Motor End | 1
Actuator Pin - Finger End | 1
Actuator Pin - Motor End | 1
Actuator Strap | 1
Bolt Head | 4
Button Pusher | 1
Button Strap | 1
Electronics Box | 1
Electronics Box Front Tab | 1
Electronics Box Side Lid | 1
Electronics Box Top Lid | 1
Fingerprint | 1
Fingerprint Base | 1
Fingerprint Bracing | 2
Fingerprint Clip | 2
Fingerprint Mount - Finger End | 1
Fingerprint Mount - Motor End | 1
Fingerprint Roller A | 1
Fingerprint Roller B | 1
Leg Connector - Finger End | 1
Leg Connector - Motor End | 1
Leg Lower | 4
Leg Upper | 4
Lock Nut | 4
Power Jack Holder | 1

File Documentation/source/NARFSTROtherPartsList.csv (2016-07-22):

Part Name | Manufacturer | Number | Quantity
10 k\ |OHgr| resistor |  |  | 3
12 mm push button\* | Sparkfun | COM-09190 | 2
12V 5A switching power supply | Adafruit | 352 | 1
20 gauge stranded wire |  |  | 1
470\ |OHgr| resistor |  |  | 3
5 cm x 7 cm double sided perfboard | Amico | s14011600am1317 | 1
Arduino Ethernet shield | Arduino | A000056 | 1
Arduino Uno R3 | Arduino | A000066 | 1
Common cathode RGB LED\* | Sparkfun | COM-00105 | 1
Female tab connector | TE Connectivity / AMP | 3-350820-2 | 3
LED Cap\* | Keystone | 8665 | 1
Linear actuator - 5" Stroke | Firgelli Automations | FA-TR-35-12-5" | 1
Male tab connector | TE Connectivity / AMP | 3-520107-2 | 3
Power pigtail female | Monoprice | 6881 | 1
Solderless banana plug female | Johnson | 108-0910-001 | 4
Solderless banana plug male | Johnson | 108-0310-001 | 4
Solid core mounting wire kit | Velleman Components | K/MOWM | 1
SPST 9 amp on off illuminated green | Jameco Valuepro | R13-66B-G-02 | 1
Switch push button SPST off momentary (on) red amp LED illuminated | Jameco Valuepro | R13-508AL-05-BRR-L3 | 1
UBEC DC/DC step-down (buck) converter - 5V @ 3A output | Adafruit | 1385 | 1
VNH5019 motor driver carrier | Pololu | 1415 | 1

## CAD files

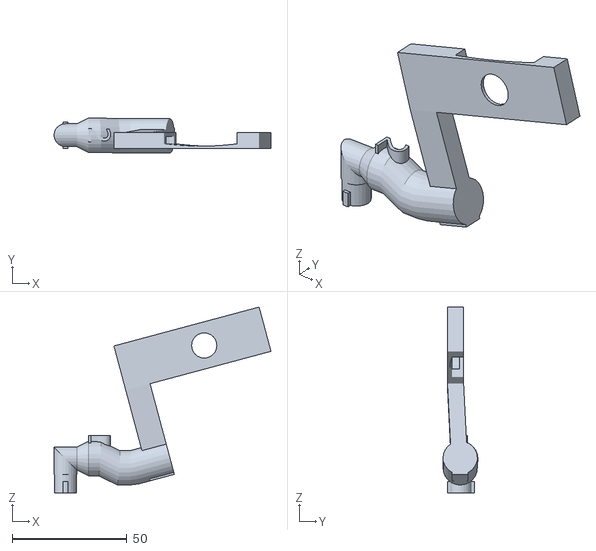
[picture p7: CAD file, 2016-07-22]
Test STL Files/Finger 2 Full.stl
94.7 x 15.3 x 81.1

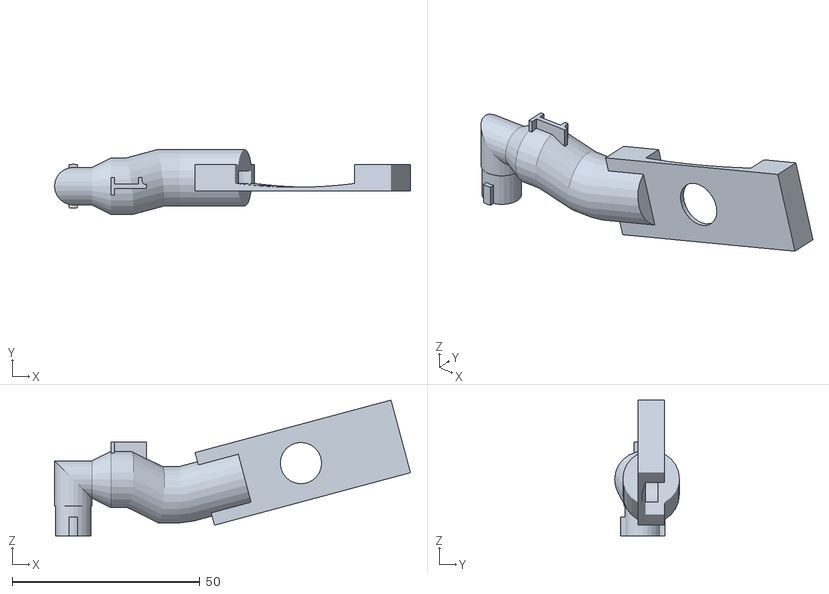
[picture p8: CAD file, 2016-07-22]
Test STL Files/Finger 1 Full.stl
94.7 x 17.2 x 36.1

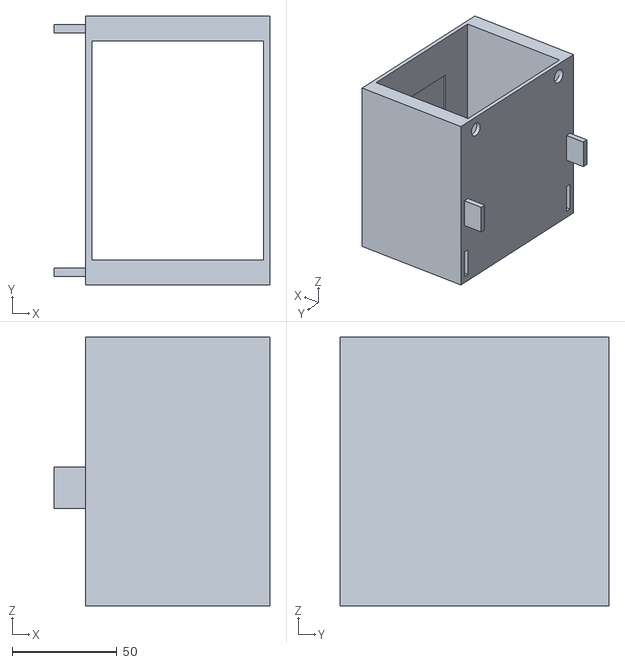
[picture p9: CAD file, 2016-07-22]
Final STL Files/NAFSTR/Main Body Print 1.stl
103.0 x 128.5 x 128.5

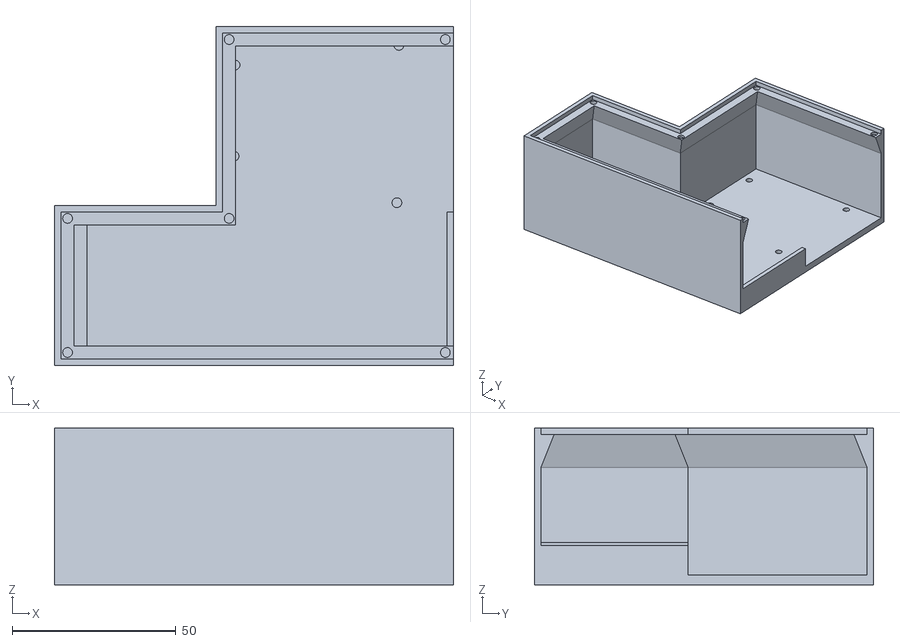
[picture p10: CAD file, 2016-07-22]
Final STL Files/NAFSTR/Arduino and Motor Box.stl
122.0 x 103.7 x 47.9

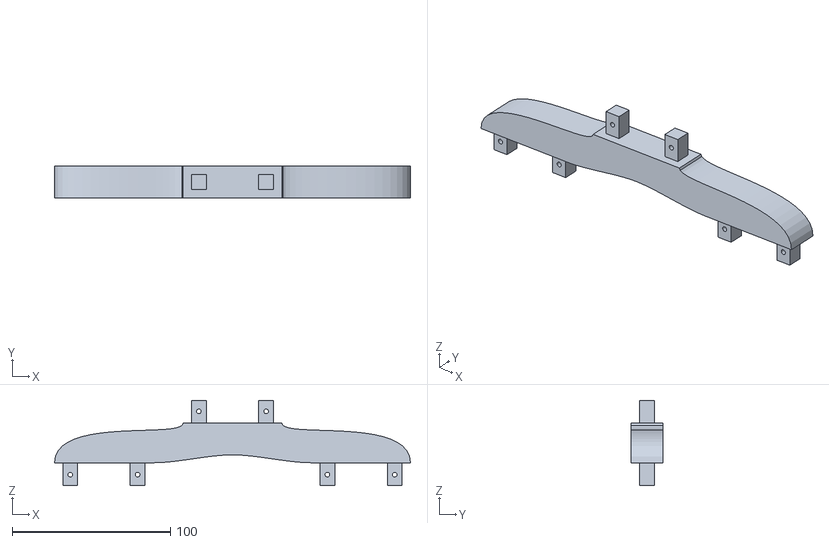
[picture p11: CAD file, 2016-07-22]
Final STL Files/NARFSTR/Leg Connector - Finger End.stl
225.2 x 20.0 x 54.0

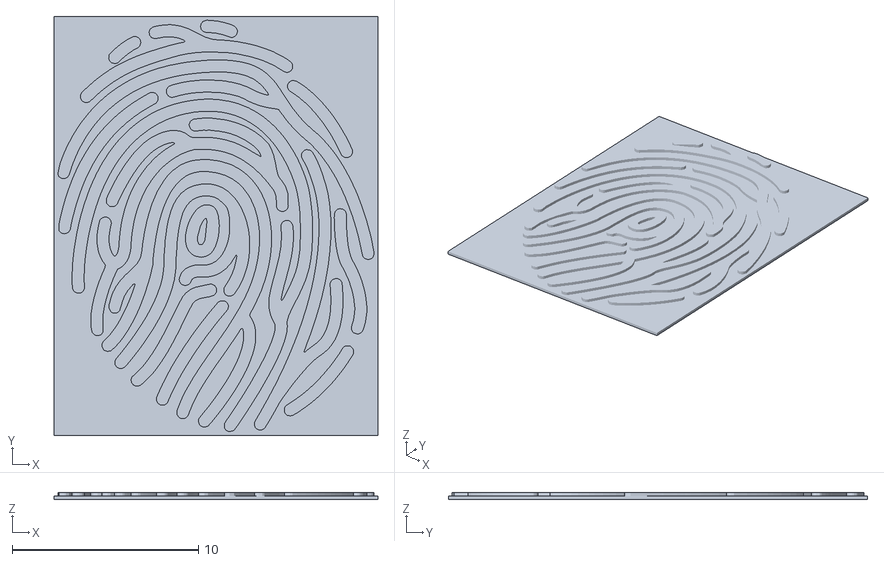
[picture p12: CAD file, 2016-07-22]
Fingerprints/NAFSTRSimpleFingerprints/Simple Fingerprint Thin.stl
17.4 x 22.5 x 0.4

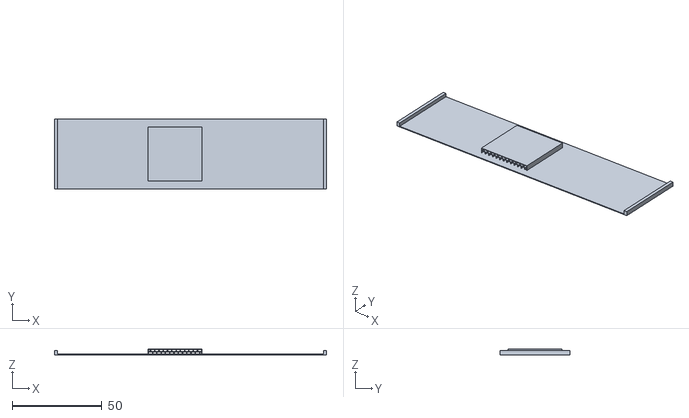
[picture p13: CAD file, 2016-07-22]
Fingerprints/NARFSTRRolledFingerprints/EmptyFingerpintLF.stl
151.5 x 39.0 x 3.20

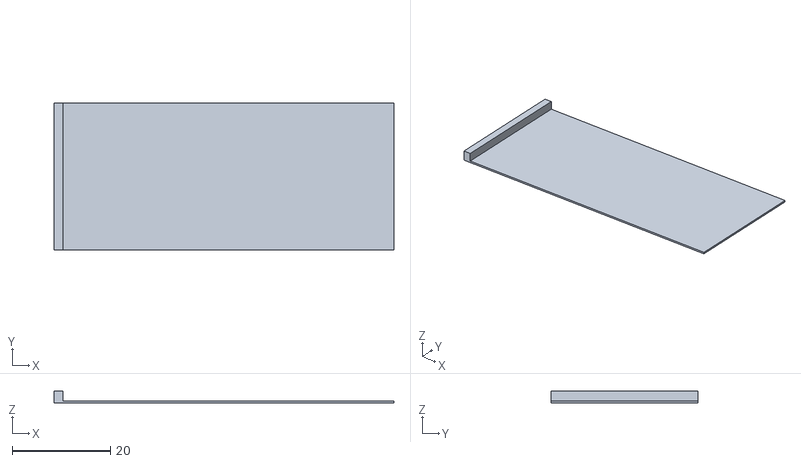
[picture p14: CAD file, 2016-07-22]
Fingerprints/NARFSTRRolledFingerprints/Test Parts/wing.stl
69.4 x 30.0 x 2.40

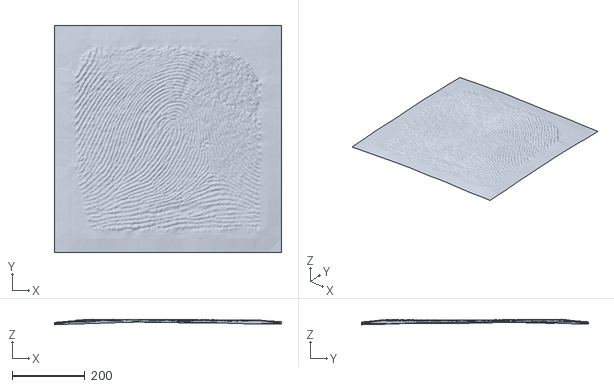
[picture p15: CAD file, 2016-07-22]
Fingerprints/PointCloudFingerprints/Fingerprint Sheet Simple.stl
623.8 x 623.8 x 15.3

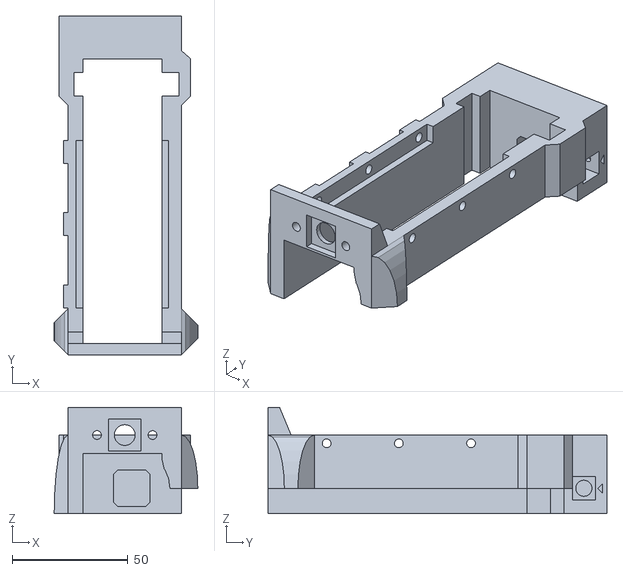
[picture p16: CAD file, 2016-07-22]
Test STL Files/Actuator Housing.stl
62.1 x 146.5 x 46.0

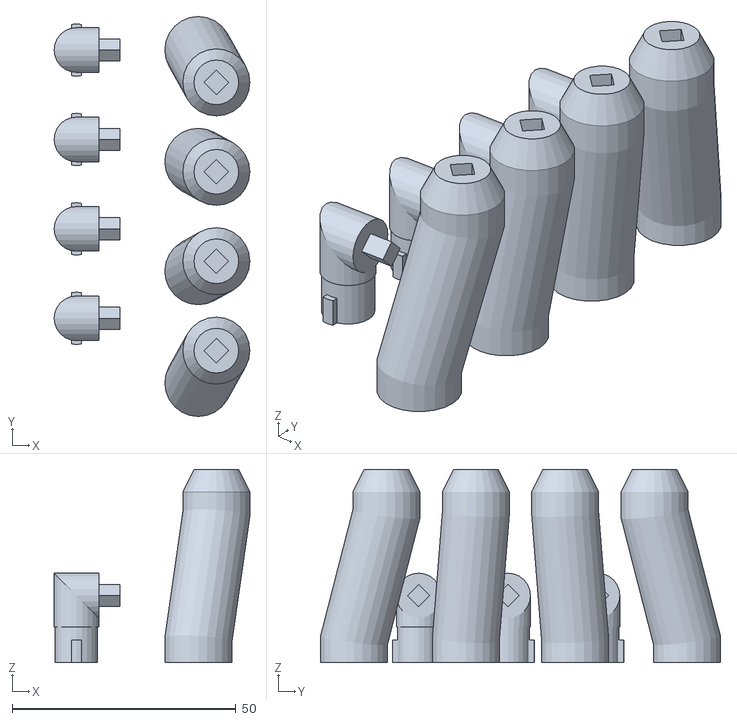
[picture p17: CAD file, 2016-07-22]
Final STL Files/NAFSTR/Fingers and Right Angles.stl
43.8 x 89.5 x 43.2

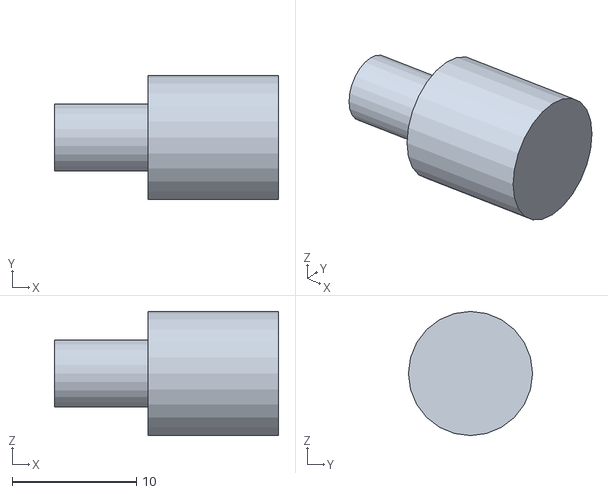
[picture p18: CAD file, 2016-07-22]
Final STL Files/NARFSTR/Fingerprint Roller A.stl
18.0 x 10.0 x 10.0

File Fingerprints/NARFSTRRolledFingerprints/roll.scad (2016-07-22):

// Fingerprint parameters
imageResolution = 19.7; //dots per mm
imageX = 416; //px
imageY = 560; //px
file = "FGen1.png";
fingerprintX = 30; //mm
fingerprintY = 30; //mm
fingerprintScale = 1.4;

//Other parameters (these should not be changed)
fingerprintRidgeHeight = .2; //mm
fingerprintBaseThickness = .2; //mm
base = .4; //mm
imageScaleFactor = 1/imageResolution;
hotFudge = 20; //mm
fingerEndWingLength = 69.365;//-X side
motorEndWingLength = 52.163;//+X side
//wingLength = 20;//4.7;
wingWidth = 1.8;
wingHeight = 2.4; //Including base, mm
spongeHeight = 3;
spongeCellWidth = 2.18;
spongeCellHeight = 1.2;
spongeWall=.2;
spongeLength = fingerprintY;
totalLength = 39;//36;

union() {
    translate([0, 0, spongeHeight+base-fingerprintBaseThickness])
        union() {
            sponge (spongeCellWidth, spongeCellHeight, spongeWall, spongeWall, fingerprintX, spongeLength, spongeHeight);
            translate([0,0,fingerprintRidgeHeight+fingerprintBaseThickness])
                fingerprint(file, fingerprintScale, fingerprintX, fingerprintY, fingerprintRidgeHeight, fingerprintBaseThickness);
        };
   // translate([fingerprintX / 2, -totalLength / 2, 0]) cube([fingerEndWingLength, totalLength, base], center = false);
    translate([-fingerprintX / 2-motorEndWingLength, -totalLength / 2, 0]) cube([motorEndWingLength+fingerprintX+fingerEndWingLength, totalLength, base], center = false);
    translate([fingerprintX / 2 + fingerEndWingLength - wingWidth, -totalLength / 2, 0]) cube([wingWidth, totalLength, wingHeight]);
    translate([-fingerprintX / 2 - motorEndWingLength, -totalLength / 2, 0]) cube([wingWidth, totalLength, wingHeight]);

    //fingerprint("FGen1.png", 1, 24, 24, .2, .2);
}

module fingerprint(fname, scale, xDim, yDim, ridgeThickness, baseThickness) {
    union() {
        intersection() {
            scale([scale,scale,1],center=true)
            resize(newsize=[imageX*imageScaleFactor,imageY*imageScaleFactor, ridgeThickness])
                surface(file = fname, center = true, invert = true);;
            cube([xDim, yDim, ridgeThickness * 2], center = true);
        }
        translate([-xDim/2, -yDim/2, -2*baseThickness])
            cube([xDim, yDim, baseThickness]);
    }
}

module sponge(holeSize, sliceSize, strutSize, slabSize, xDim, yDim, zDim) {

  n = (zDim - slabSize) / (slabSize + sliceSize);

  size = [xDim, yDim, slabSize * (n + 1) + sliceSize * n]; //x,y,z size

  translate([-xDim / 2, -yDim / 2, -( slabSize * (n + 1) + sliceSize * n)])
  union() {
    difference() {
      cube(size);

      for (z = [slabSize: sliceSize + slabSize: size[2] - slabSize]) {
        for (x = [0: holeSize + strutSize: size[0]]) {
/*
          if (round(x / (holeSize + strutSize)) % 2 == 1 && z == slabSize) {
            translate([x + strutSize, -hotFudge/2, -hotFudge])
            cube([holeSize, size[1]+hotFudge, sliceSize + slabSize+hotFudge]);
          } else
         */
          if (round((z - slabSize) / (sliceSize + slabSize)) % 2 == 0) {
            //if (x < size[0] - holeSize)o {
            translate([x + strutSize, -hotFudge/2, z])
            cube([holeSize, size[1]+hotFudge, sliceSize]);
            //}
          } else {
            translate([x - (holeSize / 2) + strutSize / 2, -hotFudge/2, z])
            cube([holeSize, size[1]+hotFudge, sliceSize]);
          }

          //echo(x = x, z = z);
        }
      }

    }
    cube([strutSize, size[1], size[2]]);
    translate([size[0] - strutSize, 0, 0])
    cube([strutSize, size[1], size[2]]);
  };
}

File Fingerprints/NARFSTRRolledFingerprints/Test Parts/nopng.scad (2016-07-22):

// Module names are of the form poly_<inkscape-path-id>().  As a result,
// you can associate a polygon in this OpenSCAD program with the corresponding
// SVG element in the Inkscape document by looking for the XML element with
// the attribute id="inkscape-path-id".

// fudge value is used to ensure that subtracted solids are a tad taller
// in the z dimension than the polygon being subtracted from.  This helps
// keep the resulting .stl file manifold.
fudge = 0.1;

module poly_path3921(h)
{
  scale([25.4 / 90, -25.4 / 90, 1]) union()
  {
    linear_extrude(height = h)
    polygon([[-13.479860, 234.610140], [-28.238790, 233.551210], [-11.176377, 229.982756], [23.499860, 225.463640], [46.977550, 221.511330], [65.562605, 216.467180], [89.128200, 211.945120], [109.198544, 210.470381], [126.407450, 211.057280], [130.315050, 211.702690], [125.907450, 213.490400], [120.206470, 214.879452], [111.473630, 215.333990], [92.334695, 216.570527], [67.957070, 220.873170], [51.243724, 224.572237], [47.999860, 226.496850], [54.873636, 227.320220], [67.499860, 225.819490], [85.179730, 222.177304], [95.999860, 220.967180], [104.499860, 220.414280], [99.499860, 221.906390], [68.924401, 228.874919], [41.999860, 231.554850], [15.499860, 233.172960], [-13.479860, 234.610140]]);
    linear_extrude(height = h)
    polygon([[-59.000140, 230.552780], [-61.500140, 229.257280], [-33.609692, 222.073523], [10.999860, 213.900440], [31.413009, 210.439797], [40.499860, 206.927060], [63.570926, 198.603392], [99.999860, 189.877050], [120.499860, 185.307460], [140.689024, 181.606816], [166.999860, 179.821380], [185.499860, 179.295790], [182.499860, 181.842550], [177.842546, 184.087785], [164.999860, 184.843850], [140.002284, 186.788171], [120.499860, 190.692400], [105.499860, 194.320760], [79.671065, 199.359977], [58.012150, 204.854100], [42.225370, 209.831020], [42.739300, 211.529300], [47.172649, 211.469367], [59.672630, 208.582520], [82.466694, 203.279401], [104.046260, 199.891070], [114.278873, 198.168449], [119.975590, 196.232040], [129.975590, 192.815290], [153.019013, 190.426134], [171.680500, 189.737160], [167.828370, 192.684900], [161.943346, 194.838049], [149.999860, 195.752640], [132.383994, 197.146095], [122.806620, 199.009290], [122.613670, 200.574010], [138.879980, 200.986400], [154.499860, 200.352840], [149.499860, 203.075040], [144.499860, 205.797240], [118.999860, 205.911440], [89.335698, 207.087320], [59.499860, 213.395540], [31.499860, 218.406870], [0.251706, 222.254382], [-30.000140, 227.519050], [-48.232792, 230.673217], [-59.000140, 230.552780]]);
    linear_extrude(height = h)
    polygon([[-80.000140, 226.669000], [-83.261800, 225.493520], [-66.029336, 219.387472], [-34.500140, 210.520810], [3.433499, 202.585052], [31.466620, 198.389860], [56.223630, 191.855170], [106.494860, 177.959710], [129.569780, 173.307236], [150.342550, 170.396590], [176.647685, 169.306879], [194.161230, 170.151230], [192.930180, 172.952920], [188.941430, 174.509179], [177.156550, 174.567920], [159.241308, 174.922174], [139.746005, 177.069635], [84.499860, 188.472200], [52.371590, 197.955560], [33.198832, 203.749806], [13.871590, 207.418740], [-26.877225, 214.850931], [-62.227000, 223.943900], [-73.624326, 226.912987], [-80.000140, 226.669000]]);
    linear_extrude(height = h)
    polygon([[-98.500140, 222.022310], [-102.500140, 220.808730], [-75.000140, 211.667870], [-34.370919, 199.391846], [2.580190, 190.857130], [18.104720, 187.066657], [37.999860, 180.187790], [80.179248, 164.742352], [106.342700, 156.412480], [124.901989, 151.344216], [135.978820, 150.389860], [160.409850, 148.785990], [183.644729, 147.720102], [204.249860, 149.063080], [207.344285, 150.010522], [207.999860, 152.316020], [207.999860, 154.986560], [199.249860, 154.118510], [182.006773, 153.547536], [160.021233, 154.285541], [138.087505, 156.058436], [120.999860, 158.592130], [97.392955, 164.869303], [68.615090, 173.969164], [42.842243, 183.151590], [28.250390, 189.676460], [20.392774, 193.213895], [0.035860, 197.413850], [-35.923540, 205.564605], [-73.316160, 216.396760], [-93.316160, 222.869600], [-98.500140, 222.022310]]);
    linear_extrude(height = h)
    polygon([[-114.750140, 217.143110], [-117.784119, 215.240441], [-113.250140, 213.834220], [-96.500140, 208.662440], [-68.023109, 198.639830], [-33.500140, 188.202290], [-9.331472, 181.632277], [3.999860, 179.364100], [21.787469, 175.845841], [54.499860, 164.174370], [95.381620, 148.764850], [126.381620, 136.438760], [138.182327, 132.156527], [151.318716, 129.196055], [166.266117, 127.478160], [183.499860, 126.923660], [203.385324, 127.632787], [207.035070, 128.779106], [208.000000, 130.685170], [208.000140, 132.889860], [183.750000, 132.942160], [164.554004, 133.357399], [150.493065, 134.688552], [139.814528, 137.208452], [130.765740, 141.189930], [105.999860, 150.908090], [62.499860, 166.400960], [23.977754, 180.238399], [4.561230, 184.981480], [-35.616574, 194.301579], [-86.659470, 210.424380], [-110.338150, 218.287760], [-114.750140, 217.143100]]);
    difference()
    {
      linear_extrude(height = h)
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

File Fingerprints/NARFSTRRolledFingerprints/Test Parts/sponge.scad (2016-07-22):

module sponge(holeSize, sliceSize, strutSize, slabSize, xDim, yDim, n) {

  size = [xDim, yDim, slabSize * (n + 1) + sliceSize * n]; //x,y,z size

  union() {
    difference() {
      cube(size);

      for (z = [slabSize: sliceSize + slabSize: size[2] - slabSize]) {
        for (x = [0: holeSize + strutSize: size[0]]) {

          if (round((z - slabSize) / (sliceSize + slabSize)) % 2 == 0) {
            //if (x < size[0] - holeSize) {
            translate([x + strutSize, 0, z])
            cube([holeSize, size[1], sliceSize]);
            //}
          } else {
            translate([x - (holeSize / 2) + strutSize / 2, 0, z])
            cube([holeSize, size[1], sliceSize]);
          }

          echo(x = x, z = z);
        }
      }

    }
    cube([strutSize, size[1], size[2]]);
    translate([size[0] - strutSize, 0, 0])
    cube([strutSize, size[1], size[2]]);
  }
}

sponge (2.18, 1.2, .2, .2, 24, 24, 3);

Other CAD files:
Test STL Files/Finger 3 Full.stl
Test STL Files/Finger 4 Full.stl
Final STL Files/NAFSTR/Finger 4 Full.stl
Final STL Files/NAFSTR/Finger 3 Full.stl
Fingerprints/NARFSTRRolledFingerprints/Test Parts/wing.scad
Final STL Files/NAFSTR/Back Faceplate.stl
Final STL Files/NAFSTR/Booster.stl
Final STL Files/NAFSTR/Bottom Plate.stl
Final STL Files/NAFSTR/Cable Tie Finger Mount.stl
Final STL Files/NAFSTR/Fingerprint Holder.stl
Final STL Files/NAFSTR/Fingers and Outside Mounts.stl
Final STL Files/NAFSTR/Front Faceplate.stl
Final STL Files/NAFSTR/Left Arm.stl
Final STL Files/NAFSTR/Left Servo Housing 1.stl
Final STL Files/NAFSTR/Plate Back.stl
Final STL Files/NAFSTR/Plate Front.stl
Final STL Files/NAFSTR/Right Arm.stl
Final STL Files/NAFSTR/Right Servo Housing 1.stl
Final STL Files/NAFSTR/Scanner Hooks.stl
Final STL Files/NAFSTR/Sensor Cable Anchor.stl
Final STL Files/NAFSTR/Sensor Cable Box.stl
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

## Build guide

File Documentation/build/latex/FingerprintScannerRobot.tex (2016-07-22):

% Generated by Sphinx.
\def\sphinxdocclass{report}
\documentclass[letterpaper,10pt,english]{sphinxmanual}
\usepackage[utf8]{inputenc}
\DeclareUnicodeCharacter{00A0}{\nobreakspace}
\usepackage{cmap}
\usepackage[T1]{fontenc}
\usepackage{babel}
\usepackage{times}
\usepackage[Bjarne]{fncychap}
\usepackage{longtable}
\usepackage{sphinx}
\usepackage{multirow}

\addto\captionsenglish{\renewcommand{\figurename}{Fig. }}
\addto\captionsenglish{\renewcommand{\tablename}{Table }}
\floatname{literal-block}{Listing }

\title{Fingerprint Scanner Robot Documentation}
\date{July 17, 2015}
\release{1.1}
\author{Jacob Glueck}
\newcommand{\sphinxlogo}{}
\renewcommand{\releasename}{Release}
\makeindex
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
\expandafter\def\csname PYG@tok@vi\endcsname{\def\PYG@tc##1{\textcolor[rgb]{0.73,0.38,0.84}{##1}}}
\expandafter\def\csname PYG@tok@nt\endcsname{\let\PYG@bf=\textbf\def\PYG@tc##1{\textcolor[rgb]{0.02,0.16,0.45}{##1}}}
\expandafter\def\csname PYG@tok@nv\endcsname{\def\PYG@tc##1{\textcolor[rgb]{0.73,0.38,0.84}{##1}}}
\expandafter\def\csname PYG@tok@s1\endcsname{\def\PYG@tc##1{\textcolor[rgb]{0.25,0.44,0.63}{##1}}}
\expandafter\def\csname PYG@tok@gp\endcsname{\let\PYG@bf=\textbf\def\PYG@tc##1{\textcolor[rgb]{0.78,0.36,0.04}{##1}}}
\expandafter\def\csname PYG@tok@sh\endcsname{\def\PYG@tc##1{\textcolor[rgb]{0.25,0.44,0.63}{##1}}}
\expandafter\def\csname PYG@tok@ow\endcsname{\let\PYG@bf=\textbf\def\PYG@tc##1{\textcolor[rgb]{0.00,0.44,0.13}{##1}}}
\expandafter\def\csname PYG@tok@sx\endcsname{\def\PYG@tc##1{\textcolor[rgb]{0.78,0.36,0.04}{##1}}}
\expandafter\def\csname PYG@tok@bp\endcsname{\def\PYG@tc##1{\textcolor[rgb]{0.00,0.44,0.13}{##1}}}
\expandafter\def\csname PYG@tok@c1\endcsname{\let\PYG@it=\textit\def\PYG@tc##1{\textcolor[rgb]{0.25,0.50,0.56}{##1}}}
\expandafter\def\csname PYG@tok@kc\endcsname{\let\PYG@bf=\textbf\def\PYG@tc##1{\textcolor[rgb]{0.00,0.44,0.13}{##1}}}
\expandafter\def\csname PYG@tok@c\endcsname{\let\PYG@it=\textit\def\PYG@tc##1{\textcolor[rgb]{0.25,0.50,0.56}{##1}}}
\expandafter\def\csname PYG@tok@mf\endcsname{\def\PYG@tc##1{\textcolor[rgb]{0.13,0.50,0.31}{##1}}}
\expandafter\def\csname PYG@tok@err\endcsname{\def\PYG@bc##1{\setlength{\fboxsep}{0pt}\fcolorbox[rgb]{1.00,0.00,0.00}{1,1,1}{\strut ##1}}}
\expandafter\def\csname PYG@tok@mb\endcsname{\def\PYG@tc##1{\textcolor[rgb]{0.13,0.50,0.31}{##1}}}
\expandafter\def\csname PYG@tok@ss\endcsname{\def\PYG@tc##1{\textcolor[rgb]{0.32,0.47,0.09}{##1}}}
\expandafter\def\csname PYG@tok@sr\endcsname{\def\PYG@tc##1{\textcolor[rgb]{0.14,0.33,0.53}{##1}}}
\expandafter\def\csname PYG@tok@mo\endcsname{\def\PYG@tc##1{\textcolor[rgb]{0.13,0.50,0.31}{##1}}}
\expandafter\def\csname PYG@tok@kd\endcsname{\let\PYG@bf=\textbf\def\PYG@tc##1{\textcolor[rgb]{0.00,0.44,0.13}{##1}}}
\expandafter\def\csname PYG@tok@mi\endcsname{\def\PYG@tc##1{\textcolor[rgb]{0.13,0.50,0.31}{##1}}}
\expandafter\def\csname PYG@tok@kn\endcsname{\let\PYG@bf=\textbf\def\PYG@tc##1{\textcolor[rgb]{0.00,0.44,0.13}{##1}}}
\expandafter\def\csname PYG@tok@o\endcsname{\def\PYG@tc##1{\textcolor[rgb]{0.40,0.40,0.40}{##1}}}
\expandafter\def\csname PYG@tok@kr\endcsname{\let\PYG@bf=\textbf\def\PYG@tc##1{\textcolor[rgb]{0.00,0.44,0.13}{##1}}}
\expandafter\def\csname PYG@tok@s\endcsname{\def\PYG@tc##1{\textcolor[rgb]{0.25,0.44,0.63}{##1}}}
\expandafter\def\csname PYG@tok@kp\endcsname{\def\PYG@tc##1{\textcolor[rgb]{0.00,0.44,0.13}{##1}}}
\expandafter\def\csname PYG@tok@w\endcsname{\def\PYG@tc##1{\textcolor[rgb]{0.73,0.73,0.73}{##1}}}
\expandafter\def\csname PYG@tok@kt\endcsname{\def\PYG@tc##1{\textcolor[rgb]{0.56,0.13,0.00}{##1}}}
\expandafter\def\csname PYG@tok@sc\endcsname{\def\PYG@tc##1{\textcolor[rgb]{0.25,0.44,0.63}{##1}}}
\expandafter\def\csname PYG@tok@sb\endcsname{\def\PYG@tc##1{\textcolor[rgb]{0.25,0.44,0.63}{##1}}}
\expandafter\def\csname PYG@tok@k\endcsname{\let\PYG@bf=\textbf\def\PYG@tc##1{\textcolor[rgb]{0.00,0.44,0.13}{##1}}}
\expandafter\def\csname PYG@tok@se\endcsname{\let\PYG@bf=\textbf\def\PYG@tc##1{\textcolor[rgb]{0.25,0.44,0.63}{##1}}}
\expandafter\def\csname PYG@tok@sd\endcsname{\let\PYG@it=\textit\def\PYG@tc##1{\textcolor[rgb]{0.25,0.44,0.63}{##1}}}

\def\PYGZbs{\char`\\}
\def\PYGZus{\char`\_}
\def\PYGZob{\char`\{}
\def\PYGZcb{\char`\}}
\def\PYGZca{\char`\^}
\def\PYGZam{\char`\&}
\def\PYGZlt{\char`\<}
\def\PYGZgt{\char`\>}
\def\PYGZsh{\char`\#}
\def\PYGZpc{\char`\%}
\def\PYGZdl{\char`\$}
\def\PYGZhy{\char`\-}
\def\PYGZsq{\char`\'}
\def\PYGZdq{\char`\"}
\def\PYGZti{\char`\~}
% for compatibility with earlier versions
\def\PYGZat{@}
\def\PYGZlb{[}
\def\PYGZrb{]}
\makeatother

\renewcommand\PYGZsq{\textquotesingle}

\begin{document}

\maketitle
\tableofcontents
\phantomsection\label{index::doc}

\chapter{Introduction}
\label{intro:introduction}\label{intro:welcome-to-fingerprint-scanner-robot-s-documentation}\label{intro::doc}
The fingerprint scanner robots are designed to automatically test fingerprint scanners. There are two robots:
\begin{enumerate}
\item {} 
NAFSTR: Networked Automated Fingerprint Scanner Test Robot. A robot with four individually-actuated fingers that simulates simple fingerprinting.

\item {} 
NARFSTR: Networked Automated Rolled Fingerprint Scanner Test Robot. A robot that simulates rolling a finger across a fingerprint scanner.

\end{enumerate}

Both robots are controlled by an Arduino Uno, and have an Arduino Ethernet Shield. They accept commands sent over USB and over a network.

\chapter{NARFSTR}
\label{NARFSTR::doc}\label{NARFSTR:narfstr}

\section{Design}
\label{NARFSTR:design}

\subsection{Structure}
\label{NARFSTR:structure}
The robot has four adjustable legs, which support a linear actuator, the electronics, and the fingerprint assembly. The following image labels all the main parts:



\subsubsection{Fingerprint Assembly}
\label{NARFSTR:fingerprint-assembly}
The fingerprint consists of a fingerprint, held by two supports. A roller rolls over the fingerprint, pressing it against the scanner. The following image shows how it works:



The linear actuator pulls the roller towards the button. As the roller moves, it compresses the fingerprint against the scanner, causing the scanner the capture a rolled print. Once the moving assembly (consisting of the roller and its support structure) hits the button, the linear actuator stops, and then reverses.

\subsubsection{Electronics Box}
\label{NARFSTR:electronics-box}
The electronics box contains openings for all the connections and buttons on the robot. The following picture shows all the main features:



There are also four more openings on the back. These are to allow the linear actuator and the button in the fingerprint assembly to connect to the electronics in the box. The following image shows these connections:



\section{Construction}
\label{NARFSTR:construction}

\subsection{Parts}
\label{NARFSTR:parts}

\subsubsection{3D Printed Parts}
\label{NARFSTR:d-printed-parts}
Almost all of the parts for the robot are 3D printed. The STL files for the parts are located in \code{Final STL Files/NARFSTR}. All of the 3D printed parts were printed in PLA except for the fingerprints. (For more information abou the fingerprints, see {\hyperref[NARFSTR:fingerprintsection]{\emph{\DUspan{}{Fingerprints}}}}.) The PLA parts were printed with a layer height of 0.2 mm using MakerBot's ``Standard'' profile. We used a MakerBot Replicator 2 and a  5$^{\text{th}}$ Generation Replicator. The following table lists each part's name and quantity.

\begin{threeparttable}
\capstart\caption{3D Printed Parts}
\label{NARFSTR:id3}
\begin{tabulary}{\linewidth}{|L|L|}
\hline
\textsf{\relax 
Part Name
} & \textsf{\relax 
Quantity
}\\
\hline
Actuator Mount - Finger End
 & 
1
\\
\hline
Actuator Mount - Motor End
 & 
1
\\
\hline
Actuator Pin - Finger End
 & 
1
\\
\hline
Actuator Pin - Motor End
 & 
1
\\
\hline
Actuator Strap
 & 
1
\\
\hline
Bolt Head
 & 
4
\\
\hline
Button Pusher
 & 
1
\\
\hline
Button Strap
 & 
1
\\
\hline
Electronics Box
 & 
1
\\
\hline
Electronics Box Front Tab
 & 
1
\\
\hline
Electronics Box Side Lid
 & 
1
\\
\hline
Electronics Box Top Lid
 & 
1
\\
\hline
Fingerprint
 & 
1
\\
\hline
Fingerprint Base
 & 
1
\\
\hline
Fingerprint Bracing
 & 
2
\\
\hline
Fingerprint Clip
 & 
2
\\
\hline
Fingerprint Mount - Finger End
 & 
1
\\
\hline
Fingerprint Mount - Motor End
 & 
1
\\
\hline
Fingerprint Roller A
 & 
1
\\
\hline
Fingerprint Roller B
 & 
1
\\
\hline
Leg Connector - Finger End
 & 
1
\\
\hline
Leg Connector - Motor End
 & 
1
\\
\hline
Leg Lower
 & 
4
\\
\hline
Leg Upper
 & 
4
\\
\hline
Lock Nut
 & 
4
\\
\hline
Power Jack Holder
 & 
1
\\
\hline\end{tabulary}

\end{threeparttable}

\subsubsection{Electronic Parts}
\label{NARFSTR:electronic-parts}
The following table lists all the electronic parts. Parts that are marked with * are close to the parts I used, but may not be exact. This is because the parts I used came from kits or other sources, and I was unable to determine their exact information. For the male and female banana plugs, 3 different colors are recommended: 1 red, 1 black, 2 blue.

\begin{threeparttable}
\capstart\caption{Electronic Parts}
\label{NARFSTR:id4}
\begin{tabulary}{\linewidth}{|L|L|L|L|}
\hline
\textsf{\relax 
Part Name
} & \textsf{\relax 
Manufacturer
} & \textsf{\relax 
Number
} & \textsf{\relax 
Quantity
}\\
\hline
10 k\(\Omega\) resistor
 &  &  & 
3
\\
\hline
12 mm push button*
 & 
Sparkfun
 & 
COM-09190
 & 
2
\\
\hline
12V 5A switching power supply
 & 
Adafruit
 & 
352
 & 
1
\\
\hline
20 gauge stranded wire
 &  &  & 
1
\\
\hline
470\(\Omega\) resistor
 &  &  & 
3
\\
\hline
5 cm x 7 cm double sided perfboard
 & 
Amico
 & 
s14011600am1317
 & 
1
\\
\hline
Arduino Ethernet shield
 & 
Arduino
 & 
A000056
 & 
1
\\
\hline
Arduino Uno R3
 & 
Arduino
 & 
A000066
 & 
1
\\
\hline
Common cathode RGB LED*
 & 
Sparkfun
 & 
COM-00105
 & 
1
\\
\hline
Female tab connector
 & 
TE Connectivity / AMP
 & 
3-350820-2
 & 
3
\\
\hline
LED Cap*
 & 
Keystone
 & 
8665
 & 
1
\\
\hline
Linear actuator - 5'' Stroke
 & 
Firgelli Automations
 & 
FA-TR-35-12-5''
 & 
1
\\
\hline
Male tab connector
 & 
TE Connectivity / AMP
 & 
3-520107-2
 & 
3
\\
\hline
Power pigtail female
 & 
Monoprice
 & 
6881
 & 
1
\\
\hline
Solderless banana plug female
 & 
Johnson
 & 
108-0910-001
 & 
4
\\
\hline
Solderless banana plug male
 & 
Johnson
 & 
108-0310-001
 & 
4
\\
\hline
Solid core mounting wire kit
 & 
Velleman Components
 & 
K/MOWM
 & 
1
\\
\hline
SPST 9 amp on off illuminated green
 & 
Jameco Valuepro
 & 
R13-66B-G-02
 & 
1
\\
\hline
Switch push button SPST off momentary (on) red amp LED illuminated
 & 
Jameco Valuepro
 & 
R13-508AL-05-BRR-L3
 & 
1
\\
\hline
UBEC DC/DC step-down (buck) converter - 5V @ 3A output
 & 
Adafruit
 & 
1385
 & 
1
\\
\hline
VNH5019 motor driver carrier
 & 
Pololu
 & 
1415
 & 
1
\\
\hline\end{tabulary}

\end{threeparttable}

\subsubsection{Screws and Miscellaneous Parts}
\label{NARFSTR:screws-and-miscellaneous-parts}
I did not order these parts, and so have limited information about them.

\begin{threeparttable}
\capstart\caption{Screws and Miscellaneous Parts}
\label{NARFSTR:id5}
\begin{tabulary}{\linewidth}{|L|L|L|}
\hline
\textsf{\relax 
Part name
} & \textsf{\relax 
Color
} & \textsf{\relax 
Quantity
}\\
\hline
19 mm diameter rubber feet
 & 
Black
 & 
8
\\
\hline
\#4 US wood screw, 15.7 mm
 & 
Gold
 & 
17
\\
\hline
\#4 US wood screw, 8.5 mm
 & 
Black
 & 
19
\\
\hline
\#8 US machine screw,  12 mm
 & 
Silver
 & 
4
\\
\hline
Epoxy
 &  & \\
\hline
Super glue
 &  & \\
\hline\end{tabulary}

\end{threeparttable}

Here is a picture of the screws:

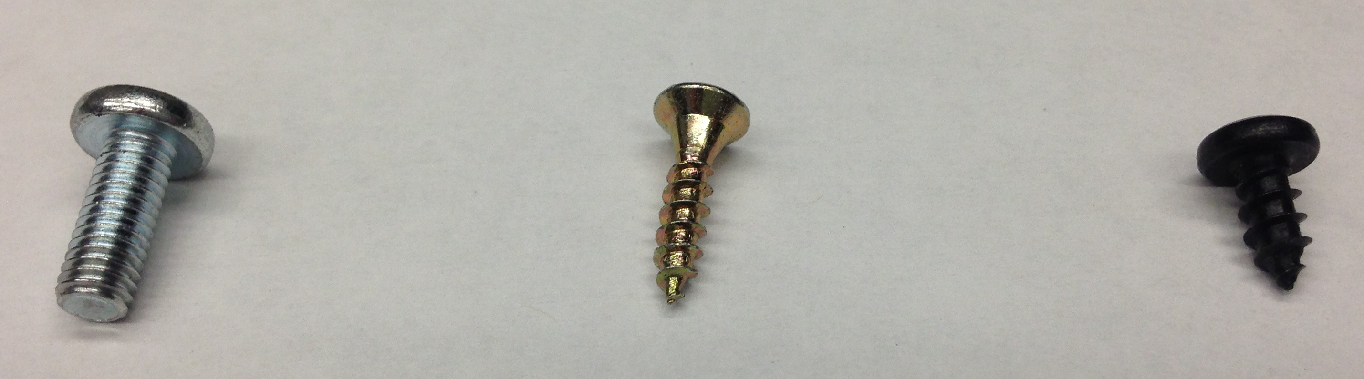
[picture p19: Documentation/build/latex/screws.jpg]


From now on, I will refer to the screws by their color.

\subsection{Legs and Actuator Mount Assembly}
\label{NARFSTR:legs-and-actuator-mount-assembly}

\subsubsection{Legs}
\label{NARFSTR:legs}
There are two leg assemblies: one on the side of the actuator with the motor, and one on the other side. Both are assembled the same way, but they use different leg adapters. To assemble a leg assembly, first screw a lock nut onto the threaded bolt in the center of the lower adjustable foot. Repeat for the other leg. Then, put an upper adjustable foot piece on top of each lower adjustable foot piece. Push down until the lock nut clicks, locking the lower part to the upper part. Then, insert a bolt head into the square hole on top of each upper adjustable foot. Screw the square head into the bolt using one of the black screws. Finally, connect each foot assembly to the lower part of a leg adapter. Secure the connection by screwing golden screws into the holes on the upper adjustable foot. Repeat this process with the other leg adapter to make the other leg assembly.



\subsubsection{Actuator Mounts}
\label{NARFSTR:actuator-mounts}
There are two actuator mounts: one for the side of the actuator with the motor, and one for the other side.

\paragraph{Motor End Actuator Mount}
\label{NARFSTR:motor-end-actuator-mount}
Slide the actuator into the mount. Insert the motor end actuator key into the hole in the actuator mount. Make sure the arrows point towards each other. Secure the key with a golden screw.



\paragraph{Finger End Actuator Mount}
\label{NARFSTR:finger-end-actuator-mount}
Slide the actuator into the mount. Insert the finger end actuator key into the hole in the actuator mount. Make sure the arrows point towards each other. Attach the top actuator strap to the actuator using two golden screws.



Insert the bottom actuator strap as shown in the diagram below. Secure it with two black screws. Finally, screw a golden screw into the hole labeled ``Screw Hole for Actuator Key'' on the diagram below. This secures the key.



Put a 12 mm push button into the button hole on the actuator mount. Secure the button using the button strap and two black screws.



Insert the finger end fingerprint mount and the motor end fingerprint mount into the bottom of the actuator mount. Secure each one with two black screws. Then, insert a fingerprint clip into each of the fingerprint mounts.



\subsubsection{Connecting the Legs and Actuator Mounts}
\label{NARFSTR:connecting-the-legs-and-actuator-mounts}
Insert the leg assemblies into the bottom of the actuator assembly. Secure each leg assembly with two golden screws.



\subsubsection{Rubber Feet}
\label{NARFSTR:rubber-feet}
Insert two rubber feet into the bottom of each foot.

\subsection{Fingerprint Assembly}
\label{NARFSTR:id1}
Glue fingerprint roller A into fingerprint roller B using super glue. Let dry. Connect fingerprint roller to moving base with the exterior finger supports. Secure each support with two black screws. Insert the button pusher into the moving base.



Attach the fingerprint assembly to the actuator by first aligning the four holes on the moving base with the holes on the actuator, ensuring that the button pusher faces the button. Then, screw a silver screw into each of the four holes on the moving base.



\subsection{Electronics Box Assembly}
\label{NARFSTR:electronics-box-assembly}
\textbf{Note:} assemble the electronics before assembling the box.

Slide Arduino Uno (with Arduino Ethernet Shield) into the box. Screw female banana plugs into holes of electronics housing. If using colors, put a red jack and a black jack into the top row, and put two blue jacks in the bottom row. Then, super glue the LED cap into the LED hole.



Super glue the front tab onto the bottom of the electronics box.



Assemble the top lid by inserting the power switch and the trigger switch into their holes. The power switch is the green rocker switch, and the trigger switch is the red push button. Using epoxy, glue a 12 mm button into the DHCP reset button hole. The square base of the button should be glued onto the plastic square on the bottom of the top lid.



Assemble the power jack by inserting a female power pigtail into the power jack holder. This may require some force. Screw power jack holder into electronics box using a black screw.



Put all other electronics into the box in the empty area behind the Arduino and put LED into LED cap. Ensure that everything is properly connected. Then, put top on box and secure with two black screws. Put back side on box and secure with one black screw. Finally, connect all cables.

\section{Electronics}
\label{NARFSTR:electronics}

\subsection{Design}
\label{NARFSTR:id2}
The robot is controlled by an Arduino Uno microcontroller. On top of the Arduino, there is an Arduino Ethernet Shield, which, through its single Ethernet port, allows the robot to connect to a network. The following components are connected to the Arduino through the header pins on the shield:
\begin{enumerate}
\item {} 
RGB LED: serves as an indicator light.

\item {} 
Trigger switch: a red pushbutton, causes the robot to move its finger back and forth when pressed.

\item {} 
Limit switch: a 12 mm push button which detects when the fingerprint has finished rolling.

\item {} 
DHCP reset button: a 12 mm push button, causes the robot to request a DHCP lease.

\item {} 
Pololu VNH5019 motor driver chip: used to drive the linear actuator.

\end{enumerate}

The robot has a single 2.1 mm DC barrel jack for power and requires 12 V DC at around 3A (estimated; based on peak motor current draw). The 12 V lines are attached directly to the motor control board, and the Arduino is powered by the output of a 5V Universal Battery Elimination Circuit (UBEC). The UBEC can produces a regulated 5 V output at a current of up to 3A. This works far better than the Arduino's built-in regulator, which, though it can handle 12 volts, gets very hot when doing so and has trouble providing the necessary current for both the Arduino and the Ethernet Shield. The robot also has a power switch, which is connected to the 12 V input line.

Here is a schematic:



There is no Ethernet Shield in the schematic, but it would be placed on top of the Arduino.

\subsection{Assembly}
\label{NARFSTR:assembly}
First, put the Arduino Ethernet Shield onto the Arduino. Then, on the 5 cm x 7 cm perfboard, assemble the circuit using the schematic above. For the motor and limit switch, which are mounted outside of the box, connect their leads to the female banana plugs, which will go into holes on the side of the electronics box. On the ends of the leads for the motor and button (which will be outside the box), attach the male banana plugs. Use the two blue plugs for the button's leads, the red one for the motor's red wire, and the black one for the motor's black wire. For the LED and other buttons, make sure they are connected with long wires so they can reach from the circuit board to their designated location in the box. Also, do not directly connect any components that will be mounted in the box directly to the circuit board. You will not be able to put the components into their holes. Instead, use the tab connectors to attach the component to the rest of the circuit. Finally, on all the 12 V lines (which, because they are connected to the motor, would have high currents), use the 20 gauge wire.

\section{Fingerprints}
\label{NARFSTR:fingerprintsection}\label{NARFSTR:fingerprints}
The fingerprints used on the robot are 3D printed. The first step in making a fingerprint is to generate a PNG image of the fingerprint. To do this, I used \href{http://biolab.csr.unibo.it/research.asp?organize=Activities\&select=\&selObj=12\&pathSubj=111\%7C\%7C12\&}{SFinGe} (http://biolab.csr.unibo.it/research.asp?organize=Activities\&select=\&selObj=12\&pathSubj=111\%7C\%7C12\&) (\textbf{S}ynthetic \textbf{Fin}gerprint \textbf{Ge}nerator) from the Biometric System Laboratory at the University of Bologna . With the program, I configured various parameters of the fingerprint, and once the ridges were generated, clicked the ``View original'' button after every step to remove all the distortion and scratches. Once the fingerprint was generated, I saved it to a bmp file and then converted it to a png.

To turn the PNG into a 3D-printable file, I wrote an OpenSCAD script, located at \code{Fingerprints/NARFSTRRolledFingerprints/roll.scad}. This script can take any black and white PNG image and produce a STL file that, when 3D printed, will fit perfectly into the robot. To use the script, configure the variables at the top of the file:

\begin{Verbatim}[commandchars=\\\{\}]
imageResolution = 19.7; //dots per mm
imageX = 416; //px
imageY = 560; //px
file = \PYGZdq{}FGen1.png\PYGZdq{};
fingerprintX = 30; //mm
fingerprintY = 30; //mm
fingerprintScale = 1.4;
\end{Verbatim}

Once these variables are configured, hit ``Preview'' in OpenSCAD to make sure everything looks good, and then hit ``Render''. This may take about an hour. Once the rendering is complete, export the file as an STL.

This script will generate a very complex 3D file which contains the fingerprint, mounted on a spongy area, which is mounted on tabs that connect to the robot. Here is a cross-sectional view of the finished product:



The two tabs at either end allow the fingerprint to be secured to the robot. The fingerprint is on top of the raised area in the middle. The holes in the raised area allow the fingerprint to compress, which results in a better scan. Here is a close up view of the holes:



To 3D print the STL file, use MakerBot Flexible Filament. Be sure to set the printing profile to the custom profile located at \code{Fingerprints/ NARFSTR Rolled Fingerprints/fingerprintprofile.txt}. The custom profile, which is based off of the MakerBot flexible filament profile, uses 1 shell and an extruder temperature of 140 °C.

\chapter{NAFSTR}
\label{NAFSTR::doc}\label{NAFSTR:nafstr}
\textbf{Note:} The documentation below is sparse and needs to be improved. Have fun!

\section{Design}
\label{NAFSTR:design}
Here is an image showing the main parts of the robot:



Here is an exploded view of the robot, which is helpful for assembly:



Here is an image showing how the finger attaches to the servo and how the fingerprint attaches to the finger:



Here is an image showing how the robot rests on the fingerprint scanner:



Here is a final image showing how the electronics housing is assembled:



\section{Construction}
\label{NAFSTR:construction}
To construct the robot, first print appropriate quantities of the parts in \code{Final STL Files/NAFSTR}. Then, attach all the parts together and insert all the electronics. Here is a parts list of all the required parts that are not 3D printed:

\begin{threeparttable}
\capstart\caption{Parts of NAFSTR}
\label{NAFSTR:id1}
\begin{tabulary}{\linewidth}{|L|L|L|L|L|}
\hline
\textsf{\relax 
Part Name
} & \textsf{\relax 
URL
} & \textsf{\relax 
Quantity
} & \textsf{\relax 
Price
} & \textsf{\relax 
Total Price
}\\
\hline
Photoresistor GL5537 5537
 & 
\href{http://www.amazon.com/gp/product/B008QVE9BG/ref=ox\_sc\_act\_title\_1?ie=UTF8\&psc=1\&smid=A39BKDU4I2L317}{http://www.amazon.com/gp/product/B008QVE9BG/ref=ox\_sc\_act\_title\_1?ie=UTF8\&psc=1\&smid=A39BKDU4I2L317}
 & 
4
 & 
0.2475
 & 
0.99
\\
\hline
1/2'' Circular Force Sensing Resistor
 & 
\href{http://www.jameco.com/webapp/wcs/stores/servlet/Product\_10001\_10001\_2128260\_-1}{http://www.jameco.com/webapp/wcs/stores/servlet/Product\_10001\_10001\_2128260\_-1}
 & 
4
 & 
7.95
 & 
31.8
\\
\hline
Hitech HS645MG Servo Motor
 & 
\href{http://www.amazon.com/Hitec-32645S-HS-645MG-Torque-Metal/dp/B003T6RSVQ}{http://www.amazon.com/Hitec-32645S-HS-645MG-Torque-Metal/dp/B003T6RSVQ}
 & 
4
 & 
49.99
 & 
199.96
\\
\hline
Arduino Uno
 & 
\href{https://www.sparkfun.com/products/11021}{https://www.sparkfun.com/products/11021}
 & 
1
 & 
24.95
 & 
24.95
\\
\hline
Arduino Ethernet Shield
 & 
\href{https://www.sparkfun.com/products/9026}{https://www.sparkfun.com/products/9026}
 & 
1
 & 
45.95
 & 
45.95
\\
\hline
Rocker Switch On Off Single Pole Single Throw Quick Connect Rocker 10 Amp 250 Volt AC Straight
 & 
\href{http://www.jameco.com/webapp/wcs/stores/servlet/Product\_10001\_10001\_316128\_-1}{http://www.jameco.com/webapp/wcs/stores/servlet/Product\_10001\_10001\_316128\_-1}
 & 
1
 & 
1.65
 & 
1.65
\\
\hline
DC Power Pigtail Female Plug
 & 
\href{http://www.monoprice.com/Product?seq=1\&format=2\&p\_id=6881\&CAWELAID=1329453851\&CAGPSPN=pla\&gclid=CjwKEAjw9eyeBRCqxc\_b-LD8kTESJADsBMxSlZYFRPGB2LwI09oGs0PsjcrUS6Nd1nQFYJR-kuWp-BoCAAjw\_wcB}{http://www.monoprice.com/Product?seq=1\&format=2\&p\_id=6881\&CAWELAID=1329453851\&CAGPSPN=pla\&gclid=CjwKEAjw9eyeBRCqxc\_b-LD8kTESJADsBMxSlZYFRPGB2LwI09oGs0PsjcrUS6Nd1nQFYJR-kuWp-BoCAAjw\_wcB}
 & 
1
 & 
0.48
 & 
0.48
\\
\hline
5V 3A UBEC
 & 
\href{http://www.adafruit.com/products/1385}{http://www.adafruit.com/products/1385}
 & 
5
 & 
9.95
 & 
49.75
\\
\hline
Multiplexer CD74HC4067E
 & 
\href{http://www.digikey.com/product-detail/en/CD74HC4067E/296-33087-5-ND/1507234}{http://www.digikey.com/product-detail/en/CD74HC4067E/296-33087-5-ND/1507234}
 & 
1
 & 
2.33
 & 
2.33
\\
\hline
1 k\(\Omega\) Resistor
 & 
\href{http://www.jameco.com/webapp/wcs/stores/servlet/Product\_10001\_10001\_690865\_-1}{http://www.jameco.com/webapp/wcs/stores/servlet/Product\_10001\_10001\_690865\_-1}
 & 
15
 & 
0.099
 & 
1.485
\\
\hline
Jumper Wires
 &  & 
100
 &  & 
0
\\
\hline
Solid Core Wire (22 Gauge)
 &  &  &  & 
0
\\
\hline
Mini Breadboard
 & 
\href{https://www.sparkfun.com/products/12043}{https://www.sparkfun.com/products/12043}
 & 
2
 & 
3.95
 & 
7.9
\\
\hline
Half Breadboard
 & 
\href{https://www.sparkfun.com/products/12002}{https://www.sparkfun.com/products/12002}
 & 
1
 & 
4.95
 & 
4.95
\\
\hline
10 \(\mu\)F Capacitor
 & 
\href{https://www.sparkfun.com/products/523}{https://www.sparkfun.com/products/523}
 & 
1
 & 
0.45
 & 
0.45
\\
\hline
10x Single Row Male and Female 40 Pin Header Strip 2.54mm / Square Pin Type, Single Row Pin Header Strips, Great Components for PCB
 & 
\href{http://www.amazon.com/Single-Female-Header-2-54mm-Components/dp/B008QUVM4E}{http://www.amazon.com/Single-Female-Header-2-54mm-Components/dp/B008QUVM4E}
 & 
1
 & 
5.24
 & 
5.24
\\
\hline
12V 5A Switching Power Supply
 & 
\href{https://www.adafruit.com/products/352}{https://www.adafruit.com/products/352}
 & 
1
 & 
24.95
 & 
24.95
\\
\hline
Total:
 &  &  &  & 
402.835
\\
\hline\end{tabulary}

\end{threeparttable}

\section{Electronics}
\label{NAFSTR:electronics}
To assemble to electronics, look at the Fritzing file located at: \code{Circuit/NAFSTRCircuit.fzz}.

\chapter{Program Development}
\label{ProgramDevelopment:program-development}\label{ProgramDevelopment::doc}
There are two programs associated with each robot: (1) a Java program that runs on a computer and controls the robot and (2) a C++ program that runs on the robot. The Java program works with both a Graphical User Interface (GUI) and the command line. With the GUI, the user specifies the actions for the robot to execute, and then connects to the robot and executes the actions. With the command line, the user can supply a text file of commands for the robot to execute, and the program will send the commands to the robot. The C++ program on the robot receives all the commands and executes them. It also responds to any button presses.

\section{Java Robot Control Program}
\label{ProgramDevelopment:java-robot-control-program}
The Java program has 3 main parts:
\begin{enumerate}
\item {} 
The back end, which handles all communication with the robot.

\item {} 
The GUI, which provides a simple way to control the robot.

\item {} 
The command line interface, which lets the user send a list of commands to the robot.

\end{enumerate}

This guide will explain each of the three parts.

\subsection{Back End}
\label{ProgramDevelopment:back-end}
The back end consists of the robot package, which contains four main classes:
\begin{enumerate}
\item {} 
\code{Robot}

\item {} 
\code{RobotCom}

\item {} 
\code{RobotInfo}

\item {} 
\code{Command}

\end{enumerate}

\code{Robot} is an abstract class, and it represents any type of robot, either a NAFSTR or a NARFSTR. It currently has one subclass, \code{NARFSTR}. The current version of the program does not support the NAFSTR robot; to control a NAFSTR, the older version must be used. \code{NARFSTR} has one constructor, which takes a \code{RobotCom} object. A \code{RobotCom} is a channel for communicating with the robot, and has methods for reading and writing data. \code{RobotCom} has two subclasses: \code{SerialRobotCom}, which represents a connection to a robot over a serial port (USB), and \code{NetworkRobotCom}, which represents a connection to a robot over a network. In order to make an instance of either class, a \code{RobotInfo} object is required. A \code{RobotInfo} object describes the type of robot, the location of the robot (an IP address and a serial port), and the robot's MAC address, which is used as an ID.

In order to easily find robots, the \code{Robot} class provides three static methods:
\begin{enumerate}
\item {} 
\code{findSerialRobots()}: finds all the robots connected over USB by checking every USB port.

\item {} 
\code{findNetworkedRobots()}: finds all the robots connected over the network by sending out a UDP broadcast and listening for responses.

\item {} 
\code{findRobots()}: finds all the robots over both USB and the network.

\end{enumerate}

In order to execute commands on a robot, the \code{Robot} class provides an \code{executeCommand(Command c)} method, and an \code{executeCommands(List\textless{}Command\textgreater{} commands)} method. Both methods send commands to the robot, and wait for execution to finish. A \code{Command} object consists of two components: a String representing the command name, and a list of Objects representing the parameters.

For more documentation, see the Javadoc, in \code{Code/FingerprintRobotControl/doc}.

\subsection{GUI}
\label{ProgramDevelopment:gui}
The code for the GUI is in three packages: \code{view}, \code{view.configurator}, and \code{view.robotpanel}. The program's GUI is an instance of \code{view.RobotController}. The \code{RobotController} class has two main components: a \code{view.robotpanel.RobotConnectionPanel}, which manages the connection with the robot, and a \code{view.robotpanel.CommandEditorPanel}, which allows the user to edit the commands being sent to the robot.

\subsection{Command Line}
\label{ProgramDevelopment:command-line}
The code for the command line interface is in \code{main.FingerprintRobotControl}. When \code{FingerprintRobotControl} is executed with no arguments, it automatically creates an instance of \code{view.RobotController}, creating the GUI. If there are arguments, it attempts to use them. The argument format is: \code{\textless{}robot type\textgreater{} \textless{}file name\textgreater{} \textless{}connection location\textgreater{}}. The robot type should be either NAFSTR of NARFSTR. (NAFSTR is not currently supported, but will be soon.) The file name should be an absolute or relative path to the file of commands which the program is to execute. The file format is a text file with one command per line. Finally, the connection location could be one of four things: ``ethernet'', ``usb'', an IP address, or a serial port. If it is ``ethernet'' or ``usb'', to program will search for robots connected over the specified channel, and pick the first one.

\section{C++ Local Control Program}
\label{ProgramDevelopment:c-local-control-program}

\subsection{Development Environment}
\label{ProgramDevelopment:development-environment}
The program was developed in Eclipse using the the Arduino Eclipse Extensions version 2.4.201506210212 by Jan Baeyens (\href{http://www.baeyens.it/eclipse/}{http://www.baeyens.it/eclipse/}), with the Arduino libraries version 1.6.5. The Robot's program consists of two parts: C++ libraries which are common to both robots (the libraries are currently only used with the NARFSTR, but should be used on the NAFSTR), and a \code{.ino} file which contains the main program for the robot. The \code{FingerprintRobotCom} library is stored in \code{Code/FingerprintRobotLocalControl/lib}. In order to make the Arduino plugin include this library (and other libraries which are stored in the lib folder) in the build path, the ``Private Library Path'' in the Arduino Plugin Preferences must be set to \code{Code/FingerprintRobotLocalControl/lib}.

\subsection{Libraries}
\label{ProgramDevelopment:libraries}
The code needs several libraries in order to compile. First, it needs the \code{FingperintRobotCom} library, which handles communication between the robot and the computer. Second, it needs the \code{EthernetNonBlocking} library, which is a modified version of the standard Arduino Ethernet Library. I modified the standard library to make the DHCP functions non-blocking. This significantly improves responsiveness; with the standard blocking DHCP functions, the robot would freeze for 60 seconds if no Ethernet cable was plugged in. Both programs also need the following standard Arduino libraries:
\begin{enumerate}
\item {} 
\code{EEPROM}

\item {} 
\code{SPI}

\end{enumerate}

Each of the NAFSTR and NARFSTR programs also require some specific libraries:

NAFSTR
\begin{enumerate}
\item {} 
\code{Servo}: standard Arduino library.

\end{enumerate}

NARFSTR
\begin{enumerate}
\item {} 
\code{Arduino-RGB-Tools}: an open-source library for controlling RGB LEDs. It is on github (\href{https://github.com/joushx/Arduino-RGB-Tools}{https://github.com/joushx/Arduino-RGB-Tools}), stored in the git repository as a submodule, and licensed under The MIT License (MIT).

\item {} 
\code{RGBConverter}:  an open-source library for converting between RGB and HSV. It is on github (\href{https://github.com/ratkins/RGBConverter}{https://github.com/ratkins/RGBConverter}), stored in the git repository as a submodule, and its license says that you can do whatever you want with it.

\item {} 
\code{VNH5019Driver}: a library I wrote for controlling the VNH5019 driver chip.

\end{enumerate}

\subsection{NARFSTR}
\label{ProgramDevelopment:narfstr}
The NARFSTR control program is located at \code{Code/FingerprintRobotLocalControl/NARFSTRLocalControl}. Its main file is \code{NARFSTRLocalControl.ino}.

\subsection{NAFSTR}
\label{ProgramDevelopment:nafstr}
The NAFSTR control program is located at \code{Code/FingerprintRobotLocalControl/NAFSTRLocalControl}. Its main file is \code{NAFSTRLocalControl.ino}. The NAFSTR program is old, and so does not use either the \code{FingerprintRobotCom} library or the \code{EthernetNonBlocking} library.

\subsection{Development Information}
\label{ProgramDevelopment:development-information}
The \code{FingerpintRobotCom} library attempts to read a MAC address from the Arduino's EEPROM on startup. If no MAC address is found, it will not work. In order to load a MAC address into EEPROM for the first time, use the \code{MACUploader} program located at \code{Code/FingerprintRobotLocalControl/MACUploader}.

\subsubsection{\texttt{FingerprintRobotCom} Library}
\label{ProgramDevelopment:fingerprintrobotcom-library}
The \code{FingerprintRobotCom} library header file (located at \code{Code/FingerprintRobotLocalControl/lib/FingerprintRobotCom/FingerprintRobotCom.h}) contains comments which explain all the important functions.

\chapter{Using the Robots}
\label{Use:using-the-robots}\label{Use::doc}
The robots are controlled by text commands send to them over either a serial connection, a TCP network connection, or a UDP network connection. These text commands can be sent in many ways. They can be sent through the Java control software, using both the command line interface and the GUI, they can be sent using Telnet or Putty, and they can be sent using serial terminal, such as gtkterm. This guide will explain the command format, and how to send commands using all the different channels.

\section{Communication Protocol}
\label{Use:communication-protocol}

\subsection{Protocol}
\label{Use:protocol}

\subsubsection{General Information}
\label{Use:general-information}\begin{enumerate}
\item {} 
The robot will receive input from a serial stream via USB or over a network connection on port 2424 (the NAFSTR uses port 80 because its software is old) via Ethernet. The format of the requests will be the same in all cases.

\item {} 
When the robot is connected over the network, it is capable of receiving requests over both a UDP connection and a TCP connection. However, if any request is received over a UDP connection, the response message will be sent over a TCP connection.

\item {} 
With the exception of UDP messages as mentioned above, the robot will respond to all messages over the channel the message was received on.

\item {} 
The robot only has a 64 byte serial buffer. Thus, if many commands are sent rapidly over USB, some commands will be lost. However, when connected over Ethernet, the robot has a 16 kibibyte buffer, thus making an overflow less likely.

\end{enumerate}

\subsubsection{Format}
\label{Use:format}\begin{enumerate}
\item {} 
Each command has the format \code{commandName arg\_0 arg\_1 arg\_2...}, where \code{arg\_n} is the n$^{\text{th}}$ argument. If the command has no arguments, then the command is simply the name. Each part of the command is separated from the others with a single space.

\item {} 
Upon receiving and successfully parsing a command, the robot will send a message of the format \code{commandName-received}. If there is a problem parsing a command, the robot will instead send \code{bad-command}.

\item {} 
Upon completion of a command, the robot will send a message of the format \code{commandName-end}.

\item {} 
When sent the string “fingerrobot”, the robot will respond with a string of the format: \code{found:robot type:MAC Address:}. For example, a NARFSTR robot with a MAC address of \code{ba:db:ad:ba:db:ad} would respond with \code{found:NARFSTR:ba:db:ad:ba:db:ad:}.

\end{enumerate}

\subsection{Commands}
\label{Use:commands}

\subsubsection{NARFSTR Commands}
\label{Use:narfstr-commands}\begin{quote}\begin{description}
\item[{Stroke}] \leavevmode\begin{quote}\begin{description}
\item[{Description}] \leavevmode
causes the robot to move the finger through one cycle.

\item[{Format}] \leavevmode
\code{stroke}

\end{description}\end{quote}

\item[{Set}] \leavevmode\begin{quote}\begin{description}
\item[{Description}] \leavevmode
sets the parameters of the robot's following moves.

\item[{Format}] \leavevmode
\code{set forwardSpeed buttonWaitTime reverseSpeed returnWaitTime}

\item[{Parameters}] \leavevmode\begin{quote}\begin{description}
\item[{\code{forwardSpeed}}] \leavevmode
the motor's speed when driving the finger away from the starting position. Between 0 and 255, inclusive.

\item[{\code{buttonWaitTime}}] \leavevmode
the amount of time, in ms, the robot should wait once the finger hits the limit switch.

\item[{\code{reverseSpeed}}] \leavevmode
the motor's speed when driving the finger back to the starting position. Between 0 and 255, inclusive.

\item[{\code{returnWaitTime}}] \leavevmode
the amount of time to wait, in ms, once the finger has returned to its original position.

\end{description}\end{quote}

\end{description}\end{quote}

\item[{Reset}] \leavevmode\begin{quote}\begin{description}
\item[{Description}] \leavevmode
causes the robot the drive the finger towards the starting position.

\item[{Format}] \leavevmode
\code{reset time speed}

\item[{Parameters}] \leavevmode\begin{quote}\begin{description}
\item[{\code{time}}] \leavevmode
the amount of time the finger will be in motion, in ms.

\item[{\code{speed}}] \leavevmode
the motor's speed, between 0 and 255 inclusive.

\end{description}\end{quote}

\end{description}\end{quote}

\end{description}\end{quote}

\subsubsection{NAFSTR Commands}
\label{Use:nafstr-commands}
See \code{DocumentationOld/Arduino - Computer Communication Protocol.docx} or \code{DocumentationOld/Arduino - Computer Communication Protocol.txt} for details.

\subsection{Examples}
\label{Use:examples}
The following are examples of what an exchange with the robot would look like.

\subsubsection{NARFSTR Example}
\label{Use:narfstr-example}
\begin{Verbatim}[commandchars=\\\{\}]
fingerrobot
found:NARFSTR:90:a2:da:0f:95:39:
set 120 2000 120 2000
set\PYGZhy{}received
set\PYGZhy{}end
stroke
stroke\PYGZhy{}received
stroke\PYGZhy{}end
reset 1000 255
reset\PYGZhy{}received
reset\PYGZhy{}end
notacommand
bad\PYGZhy{}command
\end{Verbatim}

\subsubsection{NAFSTR Example}
\label{Use:nafstr-example}
Please put one here!

\section{Control with \texttt{FingerpintRobotControl} Java Program}
\label{Use:control-with-fingerpintrobotcontrol-java-program}
The program can be found in \code{Code/FingerprintRobotControl/FingerprintRobotControl-v1.1.jar} and allows for both GUI and command line operation. The following two sections describe both methods.

\textbf{Note:} the NAFSTR uses an older version of the software, found in \code{Code/FingerprintRobotControl/FingerprintRobotControl-v1.0.jar}. Most, but not all, of the instructions below apply to the older version.

\subsection{GUI Control}
\label{Use:gui-control}
To launch the program in GUI mode, simply run the program. Or, launch the program from the command line with no arguments: \code{java -jar FingerprintRobotControl-v1.1.jar}. Once the program opens, you should see a window like the one below.

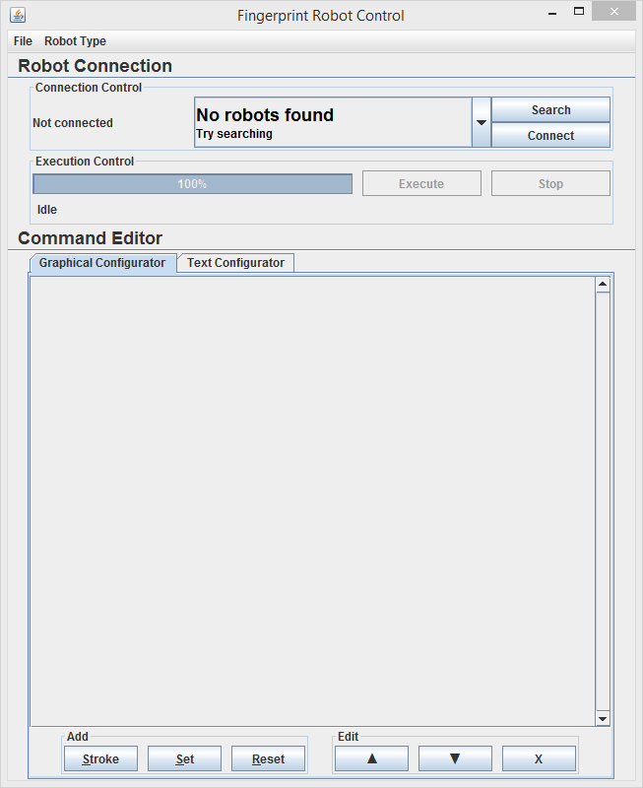
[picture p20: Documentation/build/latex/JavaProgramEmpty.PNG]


This is the starting screen. To use the program, first search for robots by clicking the ``Search'' button. After about three seconds, the combo box will be populated with the types, locations, and MAC addresses of all the robots the program found. To connect to a robot, select one from the list and press connect. If the connection was successful, the status field to the left of the combo box should say ``Connected''.

Now, you can begin to write the commands you want the robot to execute. There are two ways to do this: (1) using the graphical configurator, which requires no knowledge of the communication protocol or, (2), using the text configurator, which allows you to simply type the commands you wish to send to the robot. To use the graphical configurator, press the button on the bottom of the screen with the name of the command you wish to add. A command should show up on the screen. Now, type in the specified values. A complete graphical program looks like the one below.

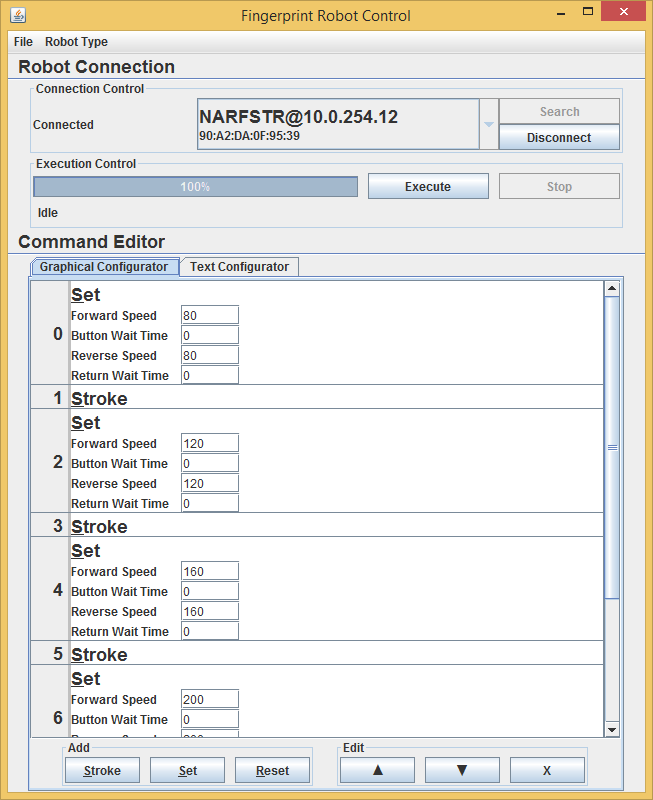
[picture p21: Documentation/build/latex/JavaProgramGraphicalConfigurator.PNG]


To use the text configurator, select the tab labeled ``Text Configurator''. If you have a program currently open if the graphical configurator, it will automatically be converted to text and displayed in the text configurator. This is a good way to learn the text format of the commands. Once you are in the text configurator, simply type commands. A program written with the text configurator is shown below:

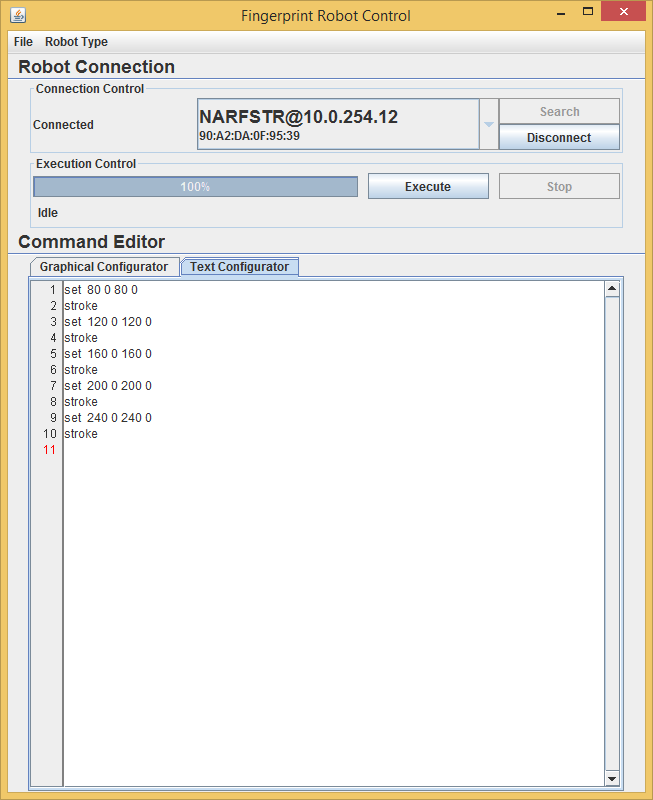
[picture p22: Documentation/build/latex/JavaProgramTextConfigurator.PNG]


Once you are done with you program, you can save it by going to ``File'' menu and clicking ``Save''. This will bring up a dialog asking you where you would like to save your file. The saved files are plain text files, with the same content that appears in the text configurator. To open a file, choose ``Open'' from the ``File'' menu. When you open a file, there will be radio buttons on the right side of the open dialog to allow you to choose the type of robot the opened file is for. (Currently, there is only one button for the NARFSTR. Support will be added for the NAFSTR in the future.) The picture below shows the open dialog.

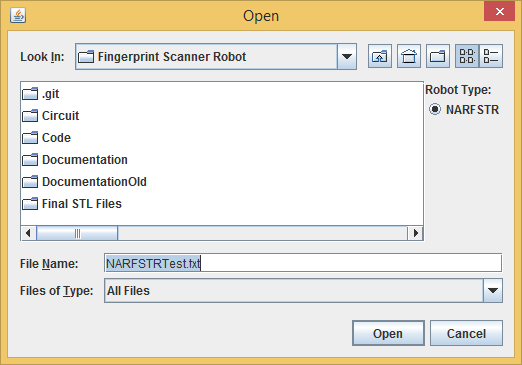
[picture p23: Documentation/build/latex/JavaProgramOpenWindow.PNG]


To execute your programs, hit the ``Execute'' button. This will send the commands to the robot. You can see the progress in the progress bar. If you want to stop execution, hit the ``Stop'' button. This will stop execution after the currently running move is complete. There is no way to stop execution in the middle of a move. If you click the stop button, and the program still says ``Stopping'' under the progress bar even though the robot has stopped, you may need to click the ``Force Stop'' button. This will immediately disconnect the robot.

\subsection{Command Line Control}
\label{Use:command-line-control}
To run the program from the command line, use the following command:

\code{java -jar FingerprintRobotControl-v1.1.jar robotType fileName connectionMode}
\begin{quote}\begin{description}
\item[{Parameters}] \leavevmode\begin{quote}\begin{description}
\item[{\code{robotType}}] \leavevmode
the type of robot to control, either NAFSTR or NARFSTR. (Currently only NARFSTR is supported.)

\item[{\code{fileName}}] \leavevmode
an absolute or relative path to a file containing the commands to execute, 1 command per line.

\item[{\code{connectionMode}}] \leavevmode\begin{quote}\begin{description}
\item[{\code{ethernet}}] \leavevmode
searches for robots on the network and connects to the first one found.

\item[{\code{usb}}] \leavevmode
searches for robots connected over USB and connects to the first one found.

\item[{IP address}] \leavevmode
the IP address of the robot to connect to.

\item[{Serial port}] \leavevmode
the name of a serial port the robot is plugged into.

\end{description}\end{quote}

\end{description}\end{quote}

\end{description}\end{quote}

\section{Control Using Telnet, Putty, and other Terminals}
\label{Use:control-using-telnet-putty-and-other-terminals}
The robot can easily be controlled using any terminal. With telnet, simply type \code{telnet ipAddress 2424}, where \code{ipAddress} is the IP address of your robot. With Putty, enter the IP address of your robot and the port 2424. Then, select telnet for the protocol and hit connect. For gtkterm, launch the terminal and select the right serial port. Once you have connected your terminal, just type commands, 1 per line, and the robot should execute them.

\renewcommand{\indexname}{Index}
\printindex
\end{document}

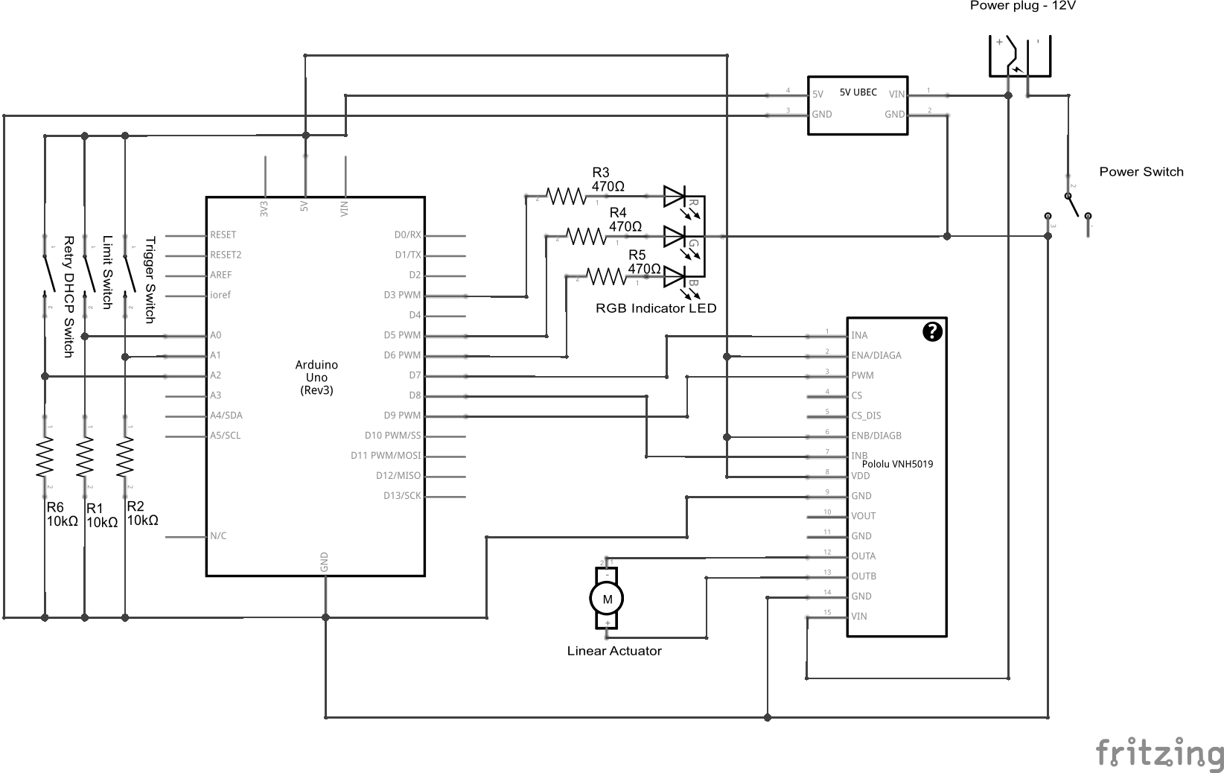
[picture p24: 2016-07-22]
Documentation/build/html/_images/NARFSTRCircuit_schem.png

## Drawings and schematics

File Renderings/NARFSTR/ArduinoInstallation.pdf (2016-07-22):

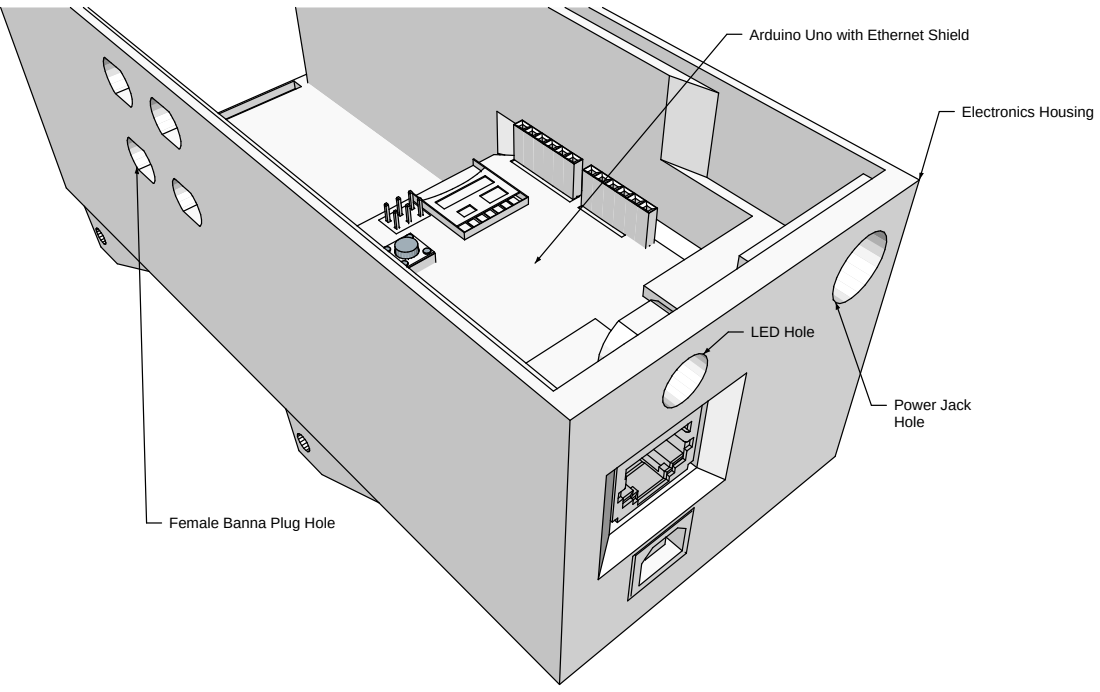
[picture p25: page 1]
Electronics Housing; LED Hole; Power Jack Hole

Arduino Uno with Ethernet Shield

Female Banna Plug Hole

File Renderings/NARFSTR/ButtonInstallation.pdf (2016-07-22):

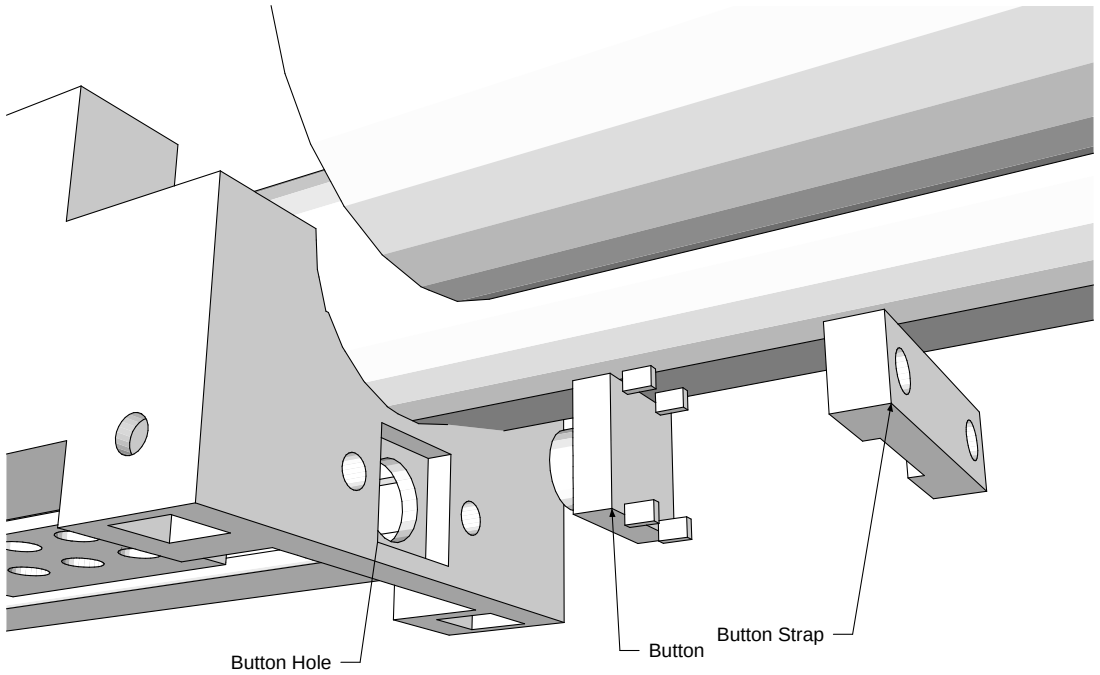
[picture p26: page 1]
Button Hole

Button Button Strap

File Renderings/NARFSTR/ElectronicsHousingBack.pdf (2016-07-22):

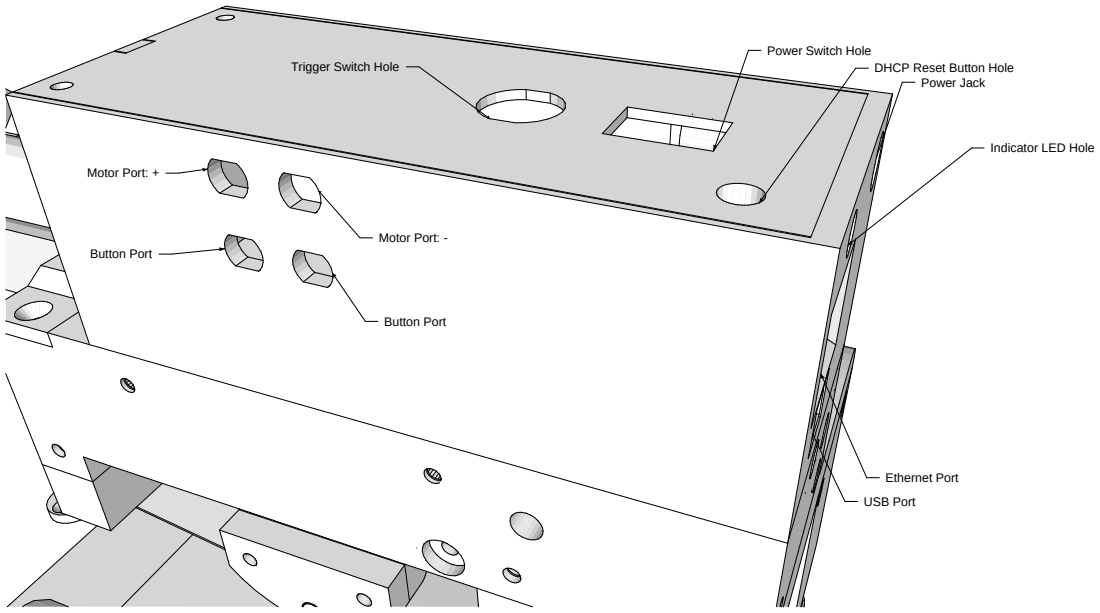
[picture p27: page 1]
Power:Jack; Ethernet:Port; USB:Port; Motor:Port::-; Motor:Port::+; Button:Port

Power:Switch:Hole

Trigger:Switch:Hole

DHCP:Reset:Button:Hole

Indicator:LED:Hole

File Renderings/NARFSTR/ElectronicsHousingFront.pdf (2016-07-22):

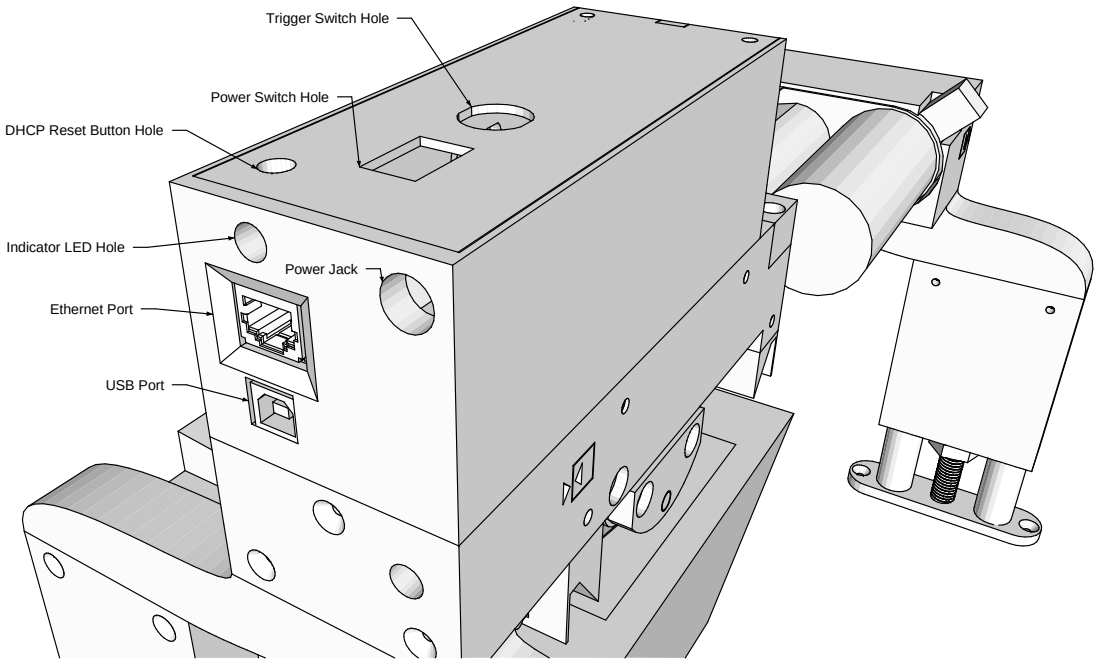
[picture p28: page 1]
Power Jack; Ethernet Port; USB Port

Trigger Switch Hole

Power Switch Hole

DHCP Reset Button Hole

Indicator LED Hole

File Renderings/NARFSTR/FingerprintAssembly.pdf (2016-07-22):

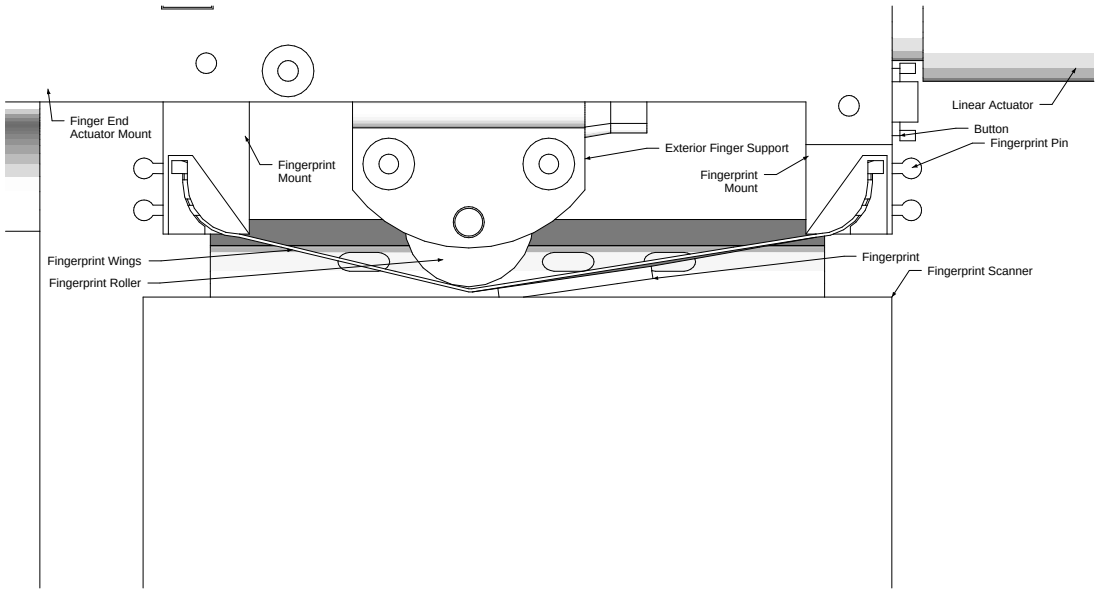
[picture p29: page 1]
Fingerprint Scanner; Finger End Actuator Mount; Fingerprint Wings; Fingerprint Roller; Button; Linear Actuator; Fingerprint; Mount

Fingerprint Pin Exterior Finger Support

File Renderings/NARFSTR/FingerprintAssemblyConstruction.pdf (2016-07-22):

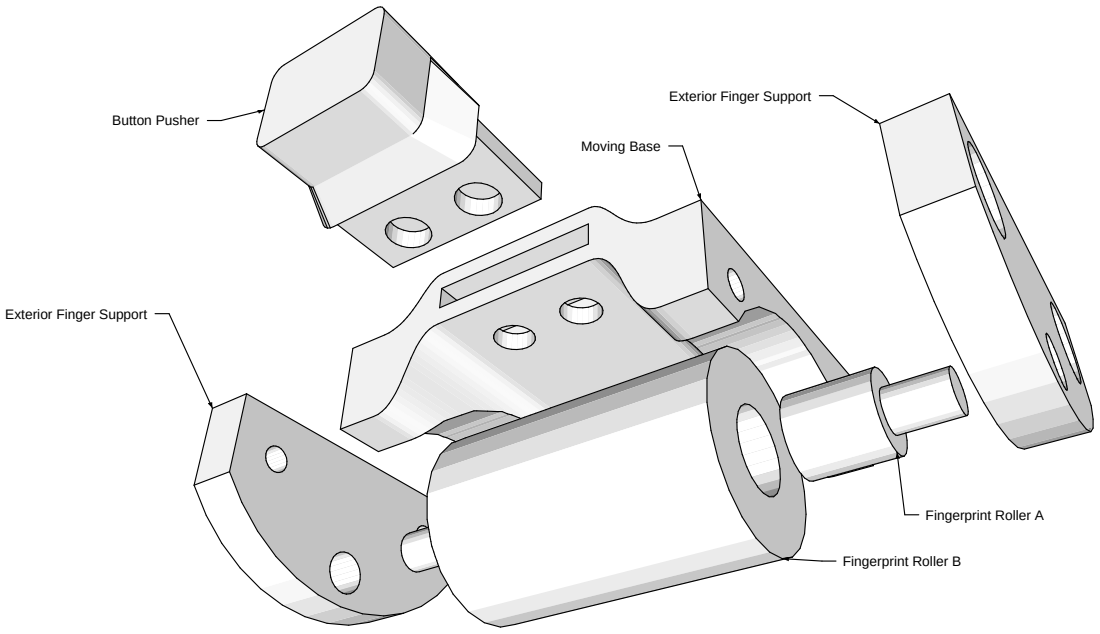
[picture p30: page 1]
Moving Base; Button Pusher; Fingerprint Roller A; Fingerprint Roller B

Exterior Finger Support

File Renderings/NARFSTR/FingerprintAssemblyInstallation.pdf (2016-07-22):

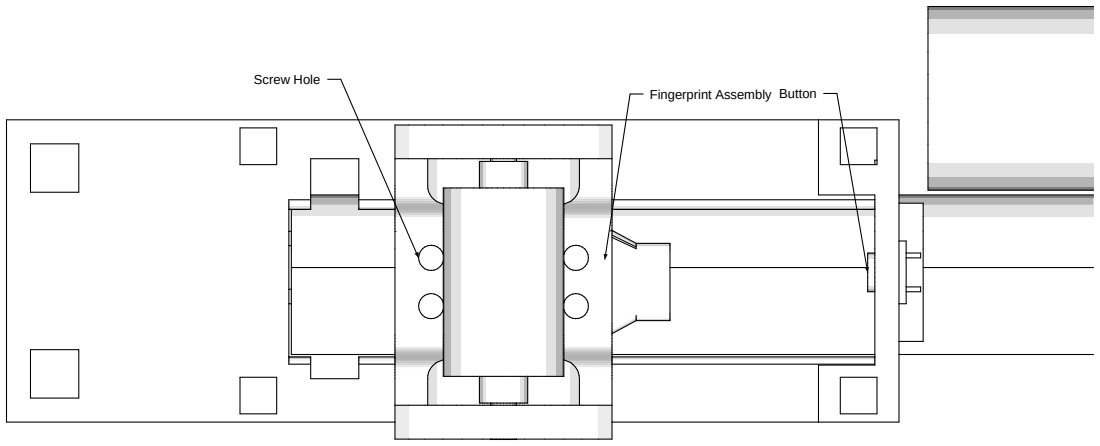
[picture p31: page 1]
Screw Hole

Fingerprint Assembly Button

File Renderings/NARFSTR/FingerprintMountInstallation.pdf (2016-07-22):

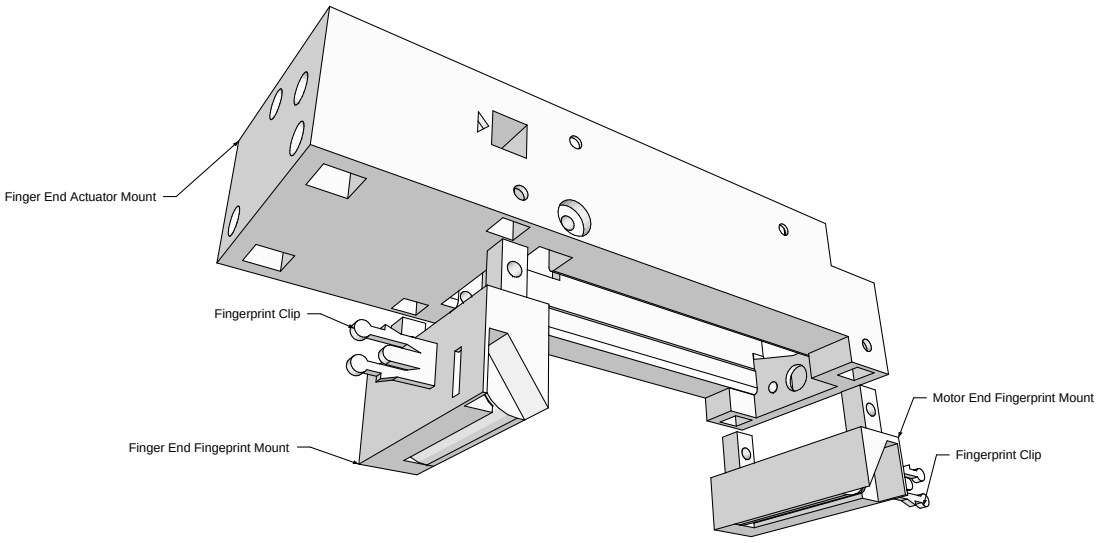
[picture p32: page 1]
Fingerprint Clip

Finger End Actuator Mount

Motor End Fingerprint Mount

Finger End Fingeprint Mount

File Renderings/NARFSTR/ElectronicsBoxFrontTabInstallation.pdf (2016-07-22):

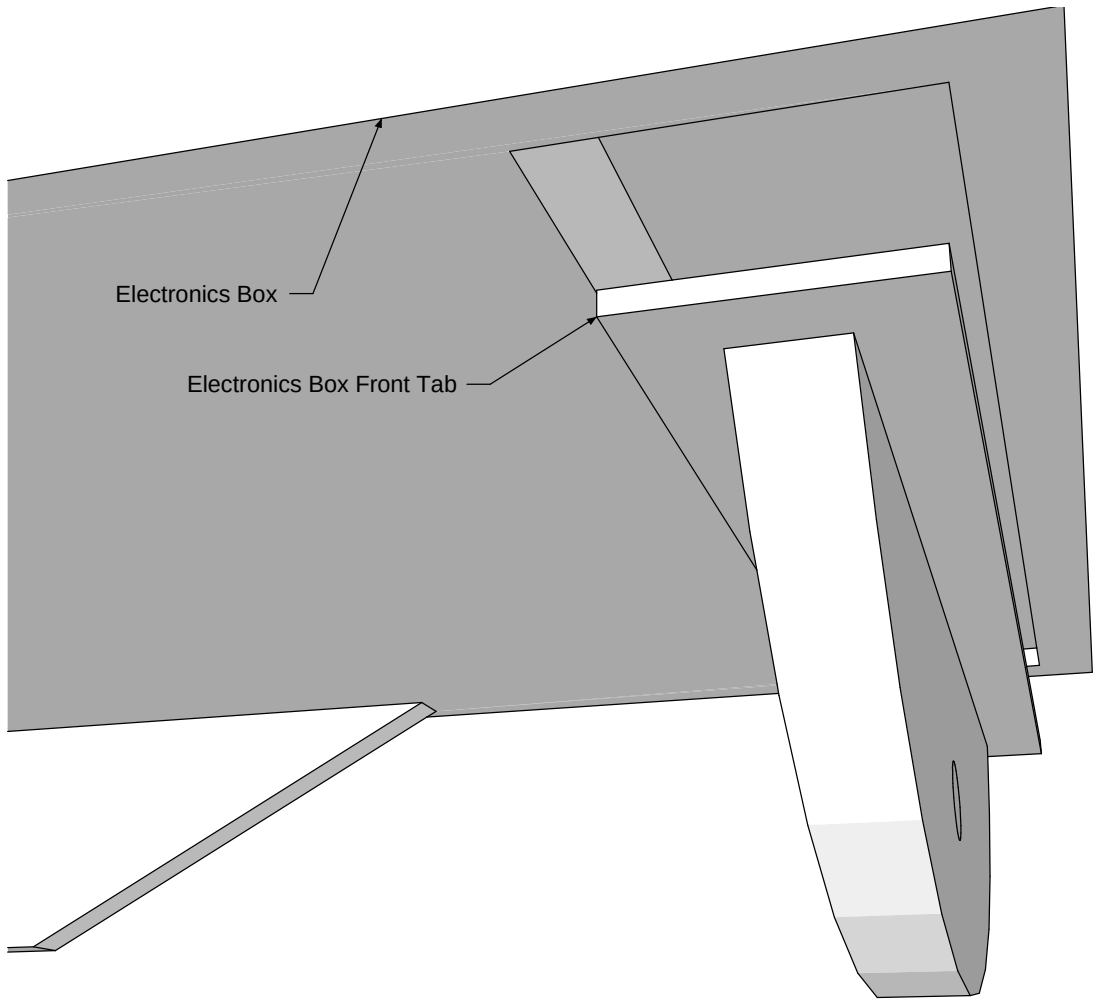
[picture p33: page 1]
Electronics Box

Electronics Box Front Tab

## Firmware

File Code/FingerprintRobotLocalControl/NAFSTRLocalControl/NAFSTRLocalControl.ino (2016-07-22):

#include <SPI.h>

#include <Dhcp.h>
#include <Dns.h>
#include <Ethernet.h>
#include <EthernetClient.h>
#include <EthernetServer.h>
#include <EthernetUdp.h>

#include <Servo.h>

//START Networking Variables ===================================

//The MAC address
byte MAC[] = {0x90, 0xA2, 0xDA, 0x0F, 0x4C, 0xD8};
//The port to write to to disable the SD card
const byte SD_PORT = 4;
//The state to write to the SD_PORT
const byte SD_STATE = HIGH;
//The port to write to to enable the Ethernet
const byte E_PORT = 10;
//The state to write to the E_PORT
const byte E_STATE = LOW;
const int TCP_PORT = 80;
//Ethernet server
EthernetServer server(TCP_PORT);
//The UDP server
EthernetUDP udp;
//The client used for sending data over tcp when the verification command was sent over udp.
EthernetClient udpReturn;
//The client used for sending data over tcp when the command came over tcp.
EthernetClient tcpReturn;
//The port on which to listen for UDP packets
const int UDP_PORT = 80;

//END Networking Variables =====================================

//START Multiplexer Variables ==================================

//The ports for the select pins on the multiplexer
const byte NUM_SELECT_PINS = 4;
//The select pins in the order S0, S1, S2, S3
const byte SELECT_PINS[] = {A1, A2, A3, A4};
//The common IO pin from the multiplexer
const byte IO_PIN = A0;

//END Multiplexer Variables ====================================

//START Servo Variables ========================================

//The number of servos
const byte NUM_SERVOS = 4;
//The ports for each servo's control line.
const byte servoPorts[] = {
  3, 5, 6, 9
};
//The array of all the servos. To get servo i, go to servos[i-1]; servo two is located at servos[1].
Servo servos[NUM_SERVOS];
//The position used to initialize the servos
const byte INIT_SERVO_POS[NUM_SERVOS] = {
  90, 90, 106, 106
};
//The value to pass to writeMicroseconds to relax the servos
const byte RELAX_PULSE = LOW;

//END Servo Variables ========================================

//START Sensor Variables =====================================

//The number of sensors
const byte NUM_SENSORS = 4;
//The ports for each sensor
const byte lightSensorPorts[] = {
  0, 1, 2, 3
};
//The ports for each sensor
const byte forceSensorPorts[] = {
  4, 5, 6, 7
};
//The ports for each sensor
const byte buttonPorts[] = {
  8, 9, 10, 11
};
const byte activateButtonPort = 12;

//END Sensor Variables =======================================

//START Move Type Variables ==================================

//Define move types
const byte POS = 0;
const byte SEN = 1;
//Define the number of move types
const byte NUM_MOVE_TYPES = 2;
//Define an array of string move types in the same order as the constants above
const String MOVE_TYPES[NUM_MOVE_TYPES] = {
  String("pos"), String("sen")
};

//END Move Type Variables ====================================

//START Sensor Type Variables ================================

//Define sensor types
const byte FSR = 0;
const byte LDR = 1;
//Define the number of sensor types
const byte NUM_SENSOR_TYPES = 2;
//Define an array of string sensor types in the same order as the constants above
const String SENSOR_TYPES[NUM_SENSOR_TYPES] = {
  String("f"), String("l")
};

//END Sensor Type Variables ==================================

//START Verification Variables ===============================

//Define the challenge and response authentication keys
const String CHALLENGE = String("fingerrobot");
const String RESPONSE = String("youfoundme");
const String RECEIVED = String("received");
const String SYNTAX_ERROR = String("bad-command");
const String END = String("end");

//END Verification Variables =================================

//START Command Type Variables ===============================

//Define numbers that correspond to commands
const byte VERIFY = 0;
const byte SET = 1;
const byte MOVE = 2;
const byte GET = 3;
const byte RELAX = 4;
const byte HOLD = 5;
//Define the number of commands
const byte NUM_COMMANDS = 6;
//Define an array of string commands in the same order as the constants above
const String COMMANDS[NUM_COMMANDS] = {
  CHALLENGE, String("set"), String("move"), String("get"), String("relax"), String("hold")
};
const byte BAD_COMMAND = -1;
const byte EMPTY_COMMAND = -2;

//END Command Type Variables =================================

//START Move Variables =======================================

//Define a null move
const byte NO_MOVE = -1;
const byte MOVE_TYPE_LOC = 0;
//The move matrix. Each row of the matrix is a move parameter; row 0 is the position 1, row 1 is wait time, and row 2 is position 2. Each column represents a servo.
int moveMatrix[2][NUM_SERVOS][6];
//Holds the move start time
long startTime;
//Holds start positions for the servos
byte startPos[NUM_SERVOS];
const byte NO_DATA = -1;
//Holds a piece of data for each servo during moves. Should be initialized to NO_DATA before every move.
long moveData[NUM_SERVOS];

//END Move Variables =========================================

//START Communication Type Variables =========================

const byte ETHERNET = 0;
const byte USB = 1;
const byte BUTTONS = 2;
const byte UDP = 3;
byte comMode;

//END Communication Type Variables ===========================

//START Communication Variables ==============================

const byte TIME_OUT = 200;

//END Communication Variables ================================

//START Other Variables ======================================

const int PARSE_INT_ERROR = 0x7fff;

//END Other Variables ========================================

//Setup method
void setup()
{

  //Attach and initialize all the servos
  for (int x = 0; x < NUM_SERVOS; x++) {
    //Attach each servo
    servos[x].attach(servoPorts[x]);
    //Send each servo the initialization postion. This seems to make them work better; sometimes they will do nothing unless they receive this.
    servos[x].write(INIT_SERVO_POS[x]);
  }

  //Fill the move matrix with null moves
  for (int x = 0; x < 2; x++) {
    for (int servo = 0; servo < NUM_SERVOS; servo++) {
      moveMatrix[x][servo][MOVE_TYPE_LOC] = NO_MOVE;
    }
  }

  //Set the select pins to output
  for (int x = 0; x < NUM_SELECT_PINS; x++) {
    pinMode(SELECT_PINS[x], OUTPUT);
  }

  //Begin serial communications
  Serial.begin(9600);
  Serial.setTimeout(TIME_OUT);

  //Disable the SD card reader
  pinMode(SD_PORT, SD_STATE);
  pinMode(E_PORT, E_STATE);

  //Begin ethernet communications
  if (Ethernet.begin(MAC) == 0) {
    Serial.println("Failed to configure Ethernet using DHCP");
  }

  //byte ip[4] = {10,0,34,100};
  //Ethernet.begin(MAC, ip);

  //Print IP address
  //Serial.println(Ethernet.localIP());

  //Start UDP
  udp.begin(UDP_PORT);

  //Start TCP
  server.begin();
  // Serial.println("READY");
}

void loop()
{

  //Check for UDP packets

  boolean ioAvailable = true;
  if ((tcpReturn = server.available())) {
    comMode = ETHERNET;
  } else if (Serial.available() > 0) {
    comMode = USB;
  }  else if (udp.parsePacket() != 0) {
    comMode = UDP;
    udpReturn.connect(udp.remoteIP(), TCP_PORT);
  } else
    ioAvailable = false;

  if (ioAvailable) {

    //Make a buffer to store the incoming command
    //As the challenge will be the longest thing read in, make the buffer the length of the challenge
    byte commandBuffer[CHALLENGE.length()];
    if (readWord(commandBuffer) != 0) {
      //Decode the command
      byte command = decode(commandBuffer, COMMANDS, NUM_COMMANDS);

      //Switch on the command
      switch (command) {
        case VERIFY:
          {
            println(RESPONSE);
            break;
          }
        case SET:
          {
            //Read in the servo number and parse the two moves
            int servoNum = parseInt();
            if (servoNum == PARSE_INT_ERROR || servoNum < 0 || servoNum >= NUM_SERVOS) {
              println(SYNTAX_ERROR);
              return;
            }
            if (!parseMove(servoNum, 0)) {
              println(SYNTAX_ERROR);
              return;
            }
            if (!parseMove(servoNum, 1)) {
              println(SYNTAX_ERROR);
              return;
            };
            println(getReceivedString(SET));
            println(getEndString(SET));
            break;
          }
        case MOVE:
          {
            //Get the number of servos to move
            int numServos = parseInt();
            if (numServos == PARSE_INT_ERROR) {
              println(SYNTAX_ERROR);
              return;
            }

            //If it is zero, move all the servos
            if (numServos == 0)
              numServos = NUM_SERVOS;

            //Make an array that will contain the IDs of the servos to be moved
            byte toMove[numServos];

            //If some servos will not move, put only the ones that should move into the array
            if (numServos != NUM_SERVOS) {
              for (int x = 0; x < numServos; x++) {
                int servoToMove = parseInt();
                if (servoToMove == PARSE_INT_ERROR) {
                  println(SYNTAX_ERROR);
                  return;
                }
                toMove[x] = servoToMove;
              }
            }
            else {

              //Put all the servos into the array
              for (int x = 0; x < numServos; x++) {
                toMove[x] = x;
              }
            }
            println(getReceivedString(MOVE));

            //For every move stage
            for (int x = 0; x < 2; x++) {

              //Record the start time
              startTime = millis();
              //Record the starting position
              for (int servo = 0; servo < numServos; servo++) {
                startPos[toMove[servo]] = servos[toMove[servo]].read();
                moveData[toMove[servo]] = NO_DATA;
              }
              byte numDone = 0;
              boolean done[numServos];
              for (int x = 0; x < numServos; x++) {
                done[x] = false;
              }
              do {

                //Update each servo and record the number of servos that are done
                for (int servo = 0; servo < numServos; servo++) {
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

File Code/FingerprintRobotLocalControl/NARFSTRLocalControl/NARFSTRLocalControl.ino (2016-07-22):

#include <Arduino.h>
#include <FingerprintRobotCom.h>
#include <HardwareSerial.h>
#include <RGBTools/RGBTools.h>
#include <stdbool.h>
#include <stdint.h>
#include <VNH5019Driver.h>
#include <WString.h>

using namespace FingerprintRobotComLib;
using namespace VNH5019DriverLib;

//Define numbers that correspond to commands
#define COMMAND_STROKE 0
#define COMMAND_SET 1
#define COMMAND_RESET 2
#define COMMAND_VERIFY 3
//Define the number of commands
#define NUM_COMMANDS 4
//Define an array of string commands in the same order as the constants above
const String COMMANDS[NUM_COMMANDS] = { "stroke", "set", "reset", CHALLENGE };
int maxCommandLength;

//Pins
#define RGB_LED_R 3
#define RGB_LED_G 5
#define RGB_LED_B 6
#define VNH5019_INA 7
#define VNH5019_INB 8
#define VNH5019_PWM 9
#define ACUTATOR_PARITY -1
#define LIMIT_SWITCH_PIN A0
#define TRIGGER_SWITCH_PIN A1
#define NETWORKING_SWITCH_PIN A2

#define FOWARD_SPEED_LOC 0
#define BUTTON_WAIT_TIME_LOC 1
#define RETURN_SPEED_LOC 2
#define RETURN_WAIT_TIME_LOC 3
#define NUM_MOVE_PARAMETERS 4
int moveMatrix[NUM_MOVE_PARAMETERS];
#define DEFAULT_FOWARD_SPEED 120
#define DEFAULT_BUTTON_WAIT_TIME 4000
#define DEFAULT_RETURN_SPEED DEFAULT_FOWARD_SPEED
#define DEFAULT_RETURN_WAIT_TIME DEFAULT_BUTTON_WAIT_TIME
const uint32_t COLOR_RED = 0xff0000L;
const uint32_t COLOR_YELLOW = 0xffff00;
const uint32_t COLOR_PURPLE = 0xff00ff;
const uint32_t COLOR_GREEN = 0x00ff00;
const uint32_t COLOR_BLUE = 0x0000ff;
const uint32_t COLOR_AQUA = 0x00ffff;
const uint32_t COLOR_WHITE = 0xffffff;
const uint32_t COLOR_ORANGE = 0xffa500;
#define BLINK_TIME 500
//Holds the move start time
unsigned long startTime;
uint32_t nextColor = COLOR_RED;

FingerprintRobotCom narfstrCom("NARFSTR");
RGBTools indicatorLED(RGB_LED_R, RGB_LED_G, RGB_LED_B, COMMON_CATHODE);
VNH5019Driver actuator(VNH5019_INA, VNH5019_INB, VNH5019_PWM, ACUTATOR_PARITY);

bool lastTriggerSwitchState;
bool lastNetworkSwitchState;

//Setup method
void setup() {
	indicatorLED.setColor(COLOR_ORANGE);
	int ret = narfstrCom.begin();
	if (ret == MAC_ERROR || ret == DHCP_START_ERROR) {
		narfstrCom.setNetworking(false);
	}

	//Find the maximum command length
	maxCommandLength = narfstrCom.maxCommandLength(COMMANDS, NUM_COMMANDS);

	//Write default move
	moveMatrix[FOWARD_SPEED_LOC] = DEFAULT_FOWARD_SPEED;
	moveMatrix[BUTTON_WAIT_TIME_LOC] = DEFAULT_BUTTON_WAIT_TIME;
	moveMatrix[RETURN_SPEED_LOC] = DEFAULT_RETURN_SPEED;
	moveMatrix[RETURN_WAIT_TIME_LOC] = DEFAULT_RETURN_WAIT_TIME;

	lastTriggerSwitchState = false;
	lastNetworkSwitchState = false;
}

void loop() {
	//Check the DHCP status
	int dhcpStatus = narfstrCom.pollDHCP();
	if (dhcpStatus == DHCP_IN_PROGRESS)
		nextColor = COLOR_PURPLE;
	else if (dhcpStatus == DHCP_SUCCESSFUL) {
		nextColor = COLOR_GREEN;
		/*for (byte thisByte = 0; thisByte < 4; thisByte++) {
		 Serial.print(narfstrCom.localIP()[thisByte], DEC);
		 Serial.print(".");
		 }
		 Serial.println();*/
	} else if (dhcpStatus == NETWORKING_OFF)
		nextColor = COLOR_RED;
	else
		nextColor = COLOR_ORANGE;

	if (wasPulse(&lastTriggerSwitchState, isButtonDown(TRIGGER_SWITCH_PIN)))
		stroke();
	if(wasPulse(&lastNetworkSwitchState, isButtonDown(NETWORKING_SWITCH_PIN)))
		narfstrCom.retryDHCP();

//	Serial.println(millis());

//Check to see if there is any data and respond to UDP discovery requests.
	checkForData();
	indicatorLED.setColor(nextColor);
}
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
